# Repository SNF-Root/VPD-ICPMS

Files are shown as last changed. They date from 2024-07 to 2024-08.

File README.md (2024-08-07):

# Low-Cost, DIY Vapor Phase Decomposition (VPD) Scanner for Trace Metal Detection on Surface of Wafers

*Insert GIF of the scanner operating*

## Introduction
Vapor phase decomposition (VPD) is a process used in the semiconductor industry to quantify trace metal contaminants on the surface of wafers. This GitHub repo provides the first open-source instructions to manufacture, program, and install a VPD capable of XXX atoms/CM^2 measurements for academic cleanrooms. 

This project was created by Alex Denton, Trevor, and Thomas Rimer at the [Stanford Nanofabrication Facility](https://snf.stanford.edu/). All ICP-MS analysis was performed by Karrie Weaver and Kathleen Akbar at the [SIGMA lab](https://sigmalab.stanford.edu/).

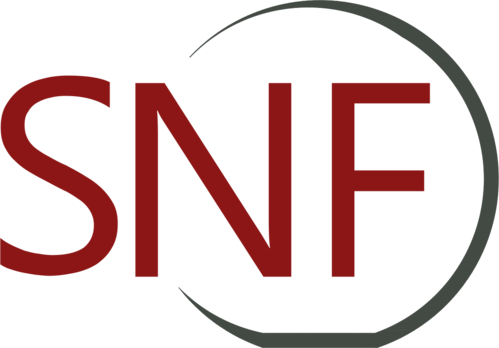
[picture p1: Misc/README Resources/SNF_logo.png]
SNF Logo
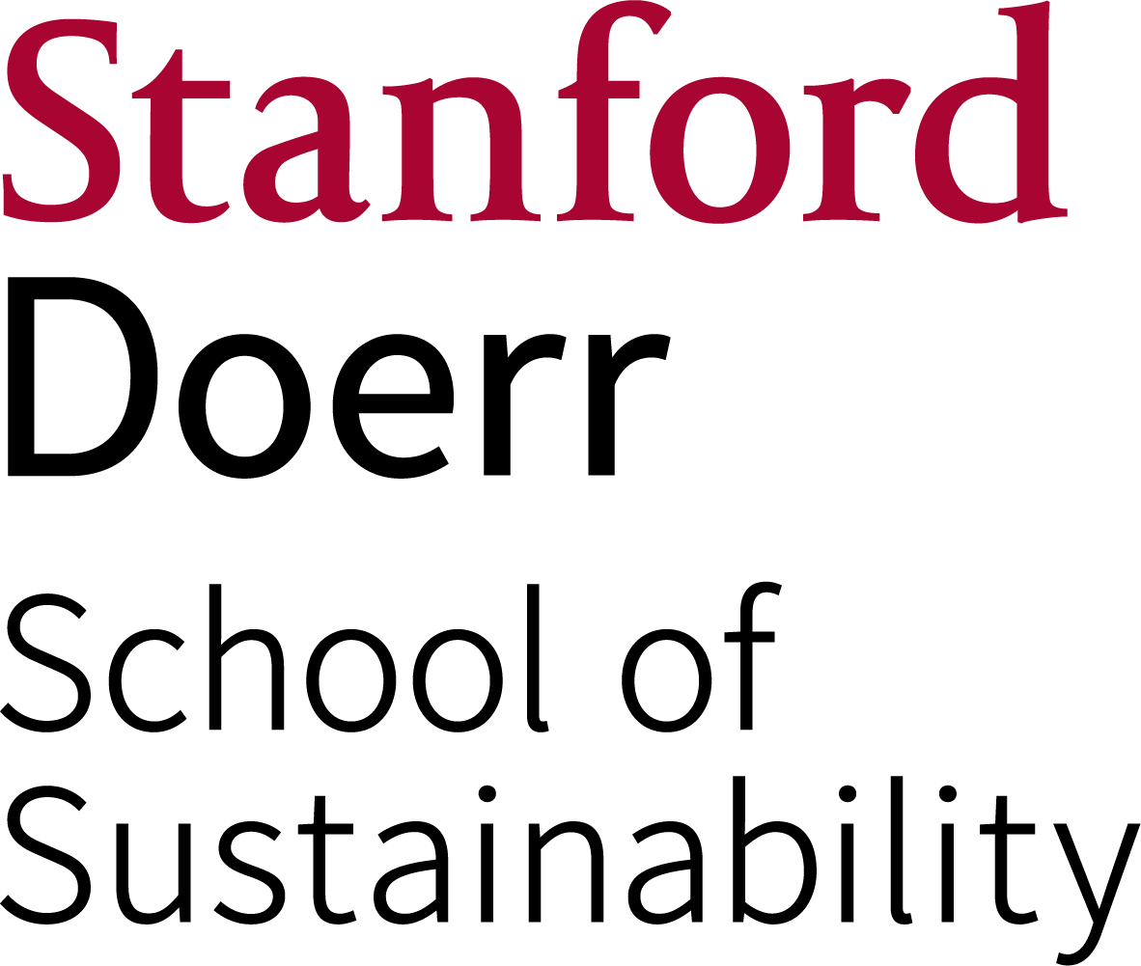
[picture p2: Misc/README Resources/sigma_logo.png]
SIGMA Logo
 

## Overview

*Insert image of the scanner sitting inside its box in a fume hood*

VPD (vapor phase decomposition) is a technique to collect metal and chemical contamininats on the surface of a wafer into a liquid droplet. The details of this collection process are explained in the "Operating Principles Section" right below. Crucially, VPD *does not* involve the measurement or quantification of chemicals; it's simply a technique (among many) to collect them. That's where ICP-MS comes in...

ICP-MS stands for "Inductively Coupled Plasma Mass Spectroscopy." It's one of the most sensitive techniques for measuring the concentration of metals and other chemicals in liquid solutions. Check out [this video](https://www.youtube.com/watch?v=tP5ZKUTWiuQ) from Agilent (an ICP-MS tool manufacturer) to learn about the basic operating principles of an ICP-MS. Briefly, the liquid sample is aerosolized before getting ionized by a plasma. Metals in the solution are then sorted and counted based on their charge/mass ratio. 

When VPD and ICP-MS are combined, it's called VPD-ICP-MS. Note that VPD doesn't necessarily need to use ICP-MS for analysis; alternatives like Atomic Absorption Spectroscopy (AAS) are also common. Similarly, VPD is not the only way to collect samples for ICP-MS; anything from blood to seawater to colloidal space dust can be measured in an ICP-MS.

Using the provided instructions outlined below, the entire VPD scanner and its enclosure can be built in <XXX hours for $X,XXX. Detailed information on the VPDs performance is availible in the [Performance](#performance) section.

## Operating Principles

The VPD scanner is based on a modified 3D printer; instead of a hot-end to extrude plastic, it has a motor-controlled syringe. To scan a wafer, the syringe first aspirates ~200 uL of an HF/H2O2/Water solution. Then it lowers to the surface of the wafer and dispenses the solution, forming a droplet on the surface of the wafer. Crucially, the droplet remains connected to the tip of the syringe. Over the course of 5-15 minutes (depending on wafer size), the scanner slowly moves the syringe head in a series of expanding concentric rings, dragging the droplet across the entire surface of the wafer. The HF in the scan solution attacks the ~2nm native oxide on the wafer's surface, dissolving any contaminants on the surface (and first few layers of SiO2). Finally, the scanner sucks up the droplet from the surface and dispenses it in a collection cuvette, for later analysis by an ICP-MS.

This droplet-dragging technique is similar to what's found in commercial VPD machines. However, there are a few differences worth noting:

**Vapor Etching:** As the name "Vapor Phase Decomposition" might suggest, commerical VPDs use an HF vapor to etch the entire surface of the wafer at once, before the droplet scan commences. This VPD scanner relies on aqueous HF within the scan solution to etch and collect the contaminants at the same time, avoiding the vapor etching step.

**Full Automation:** A human user is needed for setup and sample transfer for this DIY VPD. Most commercial VPDs have fully automated setups which allow for seamless integration into production lines.

**Speed:** While our machine takes ~20+ minutes to process a wafer, a commercial machine can often complete a scan in <60 seconds.

## Imporant Notes

**Analysis**: As hinted at above, this project assumes you have access to an ICP-MS or similarly sensitive tool to analyze the samples. The VPD scanner itself has no capacity to analyze the droplets it collects. More information about the ICP-MS analysis—along with alternatives—are detailed in the XXX section below. 

**Safety**: This project relies on hydrofluoric acid (HF) for the collection solution. HF is an extremely toxic chemical; if you need to google why, this project is *not* for you.

**Setup**: This machine produces HF vapor and should therefore be operated inside a fume hood. The minimum fume hood space required is 20" wide, 25" deep, and 42" tall. Note that the enclosure built for the scanner (detailed below) is NOT a fume hood; it is a positvely pressurized chamber to keep the VPD free of contaminats. If the enclosure is placed outside of a fume hood it will pump HF fumes at the operator and surrounding environment!

## DIY VPD Instructions

The rest of this document is dedicated to the detailed instructions for fabricating, testing, and using your own DIY VPD. 

0. [Fabrication Overview](#step-0-fabrication-overview)
1. [Procurement](#procurement)
2. [Manufacturing and Assembly](#manufacturing-and-assembly)
3. [Scripting](#scripting)
4. [Characterization](#characterization)
5. [Standard Operation](#tunning-your-first-test)
6. [Misc](#mis)

## Step 0: Fabrication Overview

The fabrication, setup, and programming of the machine are as follows:
1) First, all supplies need to be purchased. This is thoroughly explained in [Procurement](#procurement)
2) Next, both parts of the VPD need to be built: the scanner (which scans the droplet) and the enclosure (which forms a clean environment around the scanner). Instructions are layed out in [Manufacturing and Assembly](#manufacturing-and-assembly)
3) After building the VPD, it needs to be programmed. [Scripting](#scripting) explains the tradeoffs between pre-generated scripts and writing custom programs.
4) With the VPD fully operational, it needs to be characterized. This involves "recovery tests" which directly measure how precise the VPD is and help diagnose hidden performance issues like contamination. The steps are outlined in [Characterization](#characterization).
5) After characterization, the VPD is ready for users! [Standard Operation](#tunning-your-first-test) offers advice on installement, intermittent calibration, and other practical guidelines for transporting samples to the ICP-MS for analysis. 
6) [Misc](#misc) contains credit and license information.

All aspects of the manufacturing process are designed to be as accessible as possible. However, it's assumed that some basic tools are availible for fabrication. Below is a list of the required materials:

- 3D printer (minimum bed size: 8" x 8" x 3")
- Laser cutter (minimum bed size: 24" x 20")
- Phillips screwdriver
- Metric allen keys
- Soldering iron
- Scissors
- Tape

### Contact Us

If you've read this far, you're probably pretty interested in VPD. Please reach out if you're thinking about building a scanner, have questions about the build process, or have issues with your own DIY-VPD! We're excited to get these into as many labs as possible! We ask you use the "Issues" tab on GitHub to ask questions (even if it's not strictly an "issue"). This will allow other people thinking of building a VPD to see who else is interested, what they're thinking, and problems they're encountering.

## Step 1: Procurement

*Every good project starts with a McMasterr Carr order; the VPD scanner is no different.*

Below are three tables, each with a set of components. The "Scanner Components" are used to build the scanner itself. The "Enclosure Components" are used to build the enclosure around the scanner. The "Experimentation Supplies" are the consumables needed to actually run experiments. All prices are approximate, as of July 2024.

All components in the first two tables can be purchased from  McMaster Carr or Amazon. However, the strict purity requirements for the sample collection means many of the experimentation supplies must be ordered directly from suppliers.

Note that each section has dropdowns that go into further detail on different items, including alternative recommendations.

### Scanner Components
| Item | Price per Unit | Units | Subcost | Link | Use
|----------|----------|----------|----------|----------|----------|
| Ender 3 3D Printer    | $249     | 1     | $168 | [Amazon](https://www.amazon.com/Comgrow-Creality-Ender-Aluminum-220x220x250mm/dp/B07BR3F9N6/) | Sacrifical 3D printer converted into the scanner
| Filament    | $25     | 1     | $25 | [Amazon](https://www.amazon.com/HATCHBOX-Printer-Filament-Dimensional-Accuracy/dp/B09G85F1CC/?th=1) | Material used to print the necessary Ender modifications

Scanner Components Subtotal: **~$200**

<details>
  <summary> Click here for details about Scanner Components, alternatives to certain items, and other comments</summary>
   
  ### Ender 3 S1 3D Printer
  The Ender 3 is a super popular, low cost, easily modifiable 3D printer chosen for its large support community and easily accessible components.

  **Ordering notes**: Feel free to purchase the Ender 3 from any website. Note that there are different versions of the Ender 3 (Ender 3s, Ender 3 pro, etc...) Make sure you purchase the Ender 3 to ensure the syringe head 3D prints fit the gantry. If you do order from a different supplier, make sure it comes with a MicroSD card. If not,  order a micro SD card seperately.
  
  **Alternatives**: Using any other 3D printer will almost certainly mean a complete redesign of all mechanical components, including the clean enclosure (unless the alternative printer is smaller than the Ender 3). Additionally, the scan programs would no longer work, meaning you'd need to generate your own using the custom routine builder included in this repo. If there were one component in this build we'd suggest not replacing, it's the Ender 3 printer. 

  ### Filament
  **Ordering notes**: Any brand of 3D printer filament will work just fine. Because the 3D prints should never come in contact with the scan solution, it does not matter what plastic you use. We recommend PLA for its ease of printing. However, PolyMax filament from PolyMaker has repeatedly proven itself as the most durable filament based on our testing, so we think it's worth purchasing. 
  
  **Alternatives**: If you're feeling ambitious, some/all 3D printed components can be machined out of teflon. This will provide excellent chemical resistance and durability. Stanford actually has a version of the scanner with custom machined teflon components. Finding a teflon machine shop, creating engineering drawings, and managing the manufacturing process is not discussed in this guide.
</details>

### Enclosure Components
| Item | Price per Unit | Units | Subcost | Link | Use
|----------|----------|----------|----------|----------|----------|
| Acrylic Plastic Sheet    | $57     | 7     | $400 | [McMaster](https://www.mcmaster.com/8560K357/) | Clear panels cut to form enclosure walls. 24"x24", 1/4" thick
| Blower fan    | $92     | 1     | $92 | [McMaster](https://www.mcmaster.com/2059K36/) | Forces air through the filter, positively pressurizing the enclosure
| ULPA Filter    | $285     | 1     | $285 | [McMaster](https://www.mcmaster.com/5543N11/) | Removes 99.999% of particulate <0.3um in the air entering the box
| Teflon Film    | $21     | 3ft     | $63 | [McMaster](https://www.mcmaster.com/8569K63/) | Protects enclosure against HF splashes
| Slow Cure Epoxy    | $14     | 1     | $14 | [Amazon](https://www.amazon.com/Bob-Smith-Industries-BSI-205-Slow-Cure/dp/B0166FFFS4/) | Joins the acrylic side panels together
| Magnets    | $0.90     | 16     | $14 | [McMaster](https://www.mcmaster.com/5862K103/) | Magnetically joins the front panels to the enclosure box
| Fast Cure Epoxy Resin    | $5     | 1     | $5 | [Amazon](https://www.amazon.com/Gorilla-Epoxy-Minute-ounce-Syringe/dp/B001Z3C3AG/?th=1) | Bonds 3D prints to the acrylic enclosure sidewalls
| Silicone Caulk    | $7     | 1     | $7 | [Amazon](https://www.amazon.com/GE-Advanced-Silicone-Kitchen-Bathroom/dp/B0C9VYYCPB/?th=1) | Non-permanent bond for filter components
| 12v Power Supply    | $26     | 1     | $26 | [Amazon](https://www.amazon.com/LRS-200-12-Switching-Supply-Single-Output/dp/B0131UU9E2/?th=1) | Powers the blower fan and LED strips
| LED Light Strip    | $21     | 1     | $21 | [Amazon](https://www.amazon.com/TOPAI-Waterproof-Brightness-2400LEDs-Cuttable/dp/B0BVR996T2/) | Illuminates inside of the box
| Power Switch    | $8     | 1     | $8 | [Amazon](https://www.amazon.com/mxuteuk-Illuminated-Household-Appliances-MXU3-101NR/dp/B07QQ21CZD/) | Toggles power to enclosure and scanner
| Power Cable    | $6     | 1     | $6 | [Amazon](https://www.amazon.com/Amazon-Basics-Computer-Monitor-Replacement/dp/B072BYGKZZ/?th=1) | Cannabilized into master power cable for scanner and enclsoure

Enclosure Components Subtotal: **~$950**

<details>
  <summary> Click here for details about Scanner Components, alternatives to certain items, and other comments</summary>
   
  ### Acrylic Plastic Sheets

  **Ordering notes**: Minimum sheet size is 23.5" x 19.5." We recommend NOT purchasing the plastic through McMaster. Instead, find a local plastic shop or hardware store that sells acrylic sheets. We purchased all our acrylic from TAP plastics; if you're in the San Francisco Bay Area, this is by far the best place to pick up material. Local shops will also cut stocks down to a size convenient for you; for example, we had TAP cut all our acrylic down to 32"x20" sheets to fit our laser cutter. 
  
  **Alternatives**: As the most expensive building material, it's tempting to find alternatives. Theoretically, any plastic enclosure that can fit the 3D printer inside and can have holes cut in it for ventilation would work. However, the clear material makes viewing the operation of the machine much easier. 

  ### Blower Fan

  **Alternatives**: If you plan on using a different blower fan, know that there are a few important considerations. First, make sure it runs on the same voltage as the power supply (and thus by extension LED lights) to avoid needing a second PSU. Second, a multi-speed blower fan is ideal to allow standby and operating blowing speeds. Lastly, a different blower fan will need a redesigned fan shroud to couple the fan output to the ULPA filter.

  ### ULPA Filter
  
  A ULPA filter was selected over a HEPA filter for its increased filtering power. We recommend using ULPA filters to lower the chance of airborne contaimination. 

  The ULPA filter linked in the table is very large and should last for years. Base your spare ordering on that working time. For what it's worth, Stanford did not purchase any spare filters.

  **Alternatives**: If you have spare, clean ULPA filters availible from another source, feel free to use them. Just note that you will need to change both the hole size in the top of the container and fan shround to couple the blower air into the filter. Also make sure the filter is not too restrictive to air flow, else you'll need to replace the blower fan.

  ### Teflon Film

  Teflon is one of a few materials resistant to HF, so this thin sheet will sit on the bottom of the acrylic enclosure to protect it from minor HF splashes.

  **Ordering Notes**: The protective sheet used on the bottom must be made from teflon. However, any brand or supplier will work fine. 

  ### Slow Cure Epoxy

  This slow cure epoxy has a long working time allowing you to fully assemble the enclosure with epoxy in the joints before it cures.

  **Alternatives**: Any long-cure (>30 min working time) will work. For aesthetic reasons we recommend a clear-drying epoxy. When building enclosures with acrylic, it's also common to see acrylic cement used; we attempted this with our enclosure and decided not to use it due to the strict edge flatness requirements. We would discourage working with acrylic cement unless you are already familiar with it. Do NOT try and use quick curing epoxy to build the enclosure, it will set before you finish assembling the enclosure.

  ### Magnets

  **Ordering notes**: The magnets are so inexpensive we recommend ordering and using the suggested ones.

  ### Fast Curing Epoxy Resin

  Rather than the slow curing epoxy, this resin is used for joining the plastic 

  **Ordering Notes**: Brand or size of epoxy resin does not matter; it will work so long as it's a general purpose epoxy designed to bond metal and plastic.

  **Alternatives**: Feel free to not order any fast curing epoxy and instead use the slow curing epoxy. Just know you'll need to wait longer for plastic parts to adhere to the acrylic, which means you'll probably need to tape them on (rather than being able to hold them against the the walls).

  ### Silicone Caulk

  **Ordering Notes**: Brand or size of the silicone caulk does not matter; feel free to purchase from a local hardware store or use a tube laying around the lab (as long as it hasn't gone bad).

  ### Power Supply

  **Ordering Notes**: Any 12v power supply will do as long as its current rating matches or exceeds the sum of the blower fan and LED light requirements.

  **Alternatives**: If you use a different LED light strip or blower fan that does not use 12v, you will need to find a new power supply accordingly. The common, rectangular, thin power supply housing type (same as the PSU linked in the table) is preferred due to its ease of mounting on the back of the ULPA filter later on.

  ### LED Lights

  While the LED lights are not necessary, they improve visibility of the VPD scanner and make it cooler.

  **Ordering Notes**: Any LED light strip with the same voltage as the power supply will work fine.

  **Alternatives**: Any lighting (bulb, lamp, etc...) that operates on either 120v or the power supply voltage will work.

</details>

### Experimentation Supplies
| Item | Price per Unit | Units | Subcost | Link | Use
|----------|----------|----------|----------|----------|----------|
| 1mL Syringes    | $29     | 1     | $29 | [Amazon](https://www.amazon.com/Syringe-Luer-Slip-Plastic-PK100/dp/B0763KTQV5/) | Pack of 100 polyethlyne syringes. Mounts inside the scanner to aspirate, move, and dispense droplet.
| Teflon Cuvette    | $--     | -     | $-- | [Amazon]() | Sterile container for both the scan soltion and scanned droplets
| Teflon Jar    | $--     | -     | $-- | [Amazon]() | Sterile container to prepare HF and H2O2 scan solution 
| Ultrapure HF    | $---     | -     | $--- | [Amazon]() | Ultrapure 2% HF to prepare scan solution
| Ultrapure H2O2    | $---     | -     | $--- | [Amazon]() | Ultrapure H2O2 to prepare scan solution
| MS Standard Solution    | $---     | -     | $-- | [Amazon]() | Pre-made solution containing ~24 heavy metals for characterizing VPD

Experimentation Supplies Subtotal: **~$1,500**

<details>
  <summary> Click here for details about Experimentation Supplies, alternatives to certain items, and other comments</summary>
   
  TODO: Complete ordering details once testing is finished and part suppliers are finalized.

</details>

## Step 2: Manufacturing and Assembly

*Insert labeled rendering of the final assembly*

The VPD scanner has two sub assmblies; the scanner and the enclosure. Each can be built independently of the other, making it convienent to split up amongst multiple people.

There are XX 3D prints requried for this project. To minimize the amount of time spent waiting for 3D prints to finish, we recommend printing all the parts before beginning any other manufacturing and assembly. 

Tehcnically, you can 3D print all components on the Ender 3 printer purchased for the scanner. This is recommended only if you have limited access to other printers. If you decide to 3D print the components on the Ender 3, you should first fully assemble the 3D printer following the video in [Step 2.1](#step-2-1) (not skipping any steps). Then, print all components (as outlined below) before continuing on the project. Know that once you've modified the printer into the scanner, it will take around an hour to uninstall the VPD parts and restore the Ender to a print-worthy state. 

<details>
  <summary> Click here for a complete list of required 3D printed parts, their associated quantities, and recommended print settings/orientations</summary>
   
  TODO: Add the complete list of STL files and how many need to be made.

</details>

### 2.1 Scanner Manufacturing

*Insert photograph of finished scanner*

#### Step 2.1.1: Assembling the Ender 3s

The Ender 3s comes partially assembled from the factory. There are several high-quality YouTube tutorials already made outlining exactly how to assemble an Ender 3. Here's a well-made one from [3D Printing Canada](https://www.youtube.com/watch?v=dQ0q9zLygTY) (https://www.youtube.com/watch?v=dQ0q9zLygTY).

While most of the build proceeds as normal, there are a few steps you should <ins>not</ins> do:

- Do not install the spool holder.
- Do not mount the extruder stepper motor on the bracket designed for it. However, you should still wire the stepper to the controller board. The extruder stepper motor will be used later on to control the syringe.
- Similarly, do not install the spring-loaded extruder gear assembly. This is not needed for the VPD.
- Do not mount or screw in the bed leveling adjustment dials. These will be installed later.
- Do not binder-clip the Ender-branded build surface onto the print bed. Parts will mount directly onto the print bed later, so this build surface is not needed.

Save all components (and spare parts) that you do not install. You will need some of these materials later.

#### Step 2.1.2: Print and Install Parts For Wafer Holder

There are three necessary 3D printed components for the wafer holder, and an additional five optional 3D printed components:

Required
- 001_Wafer_Holder_Base.stl
- 002_Wafer_Vial_Holder_Left.stl
- 003_Wafer_Vial_Holder_Right.stl

Optional
- 004_Wafer_Holder_2_inch_Chuck.stl
- 005_Wafer_Holder_3_inch_Chuck.stl
- 006_Wafer_Holder_4_inch_Chuck.stl
- 007_Wafer_Holder_5_inch_Chuck.stl
- 008_Wafer_Holder_6_inch_Chuck.stl

<details>
  <summary> Click here for a details about 3D printing orientation and settings
  <br></br>
  </summary>
   
  TODO: Include pictures of recommended print orientation and print settings for the  components. This should be a copy from the complete 3D print list above.

</details>

At least one optional component must be printed to use the wafer holder. 

Place 001_Wafer_Holder_Base on the print bed, alligning the the holes in each corner with the screws holes in the aluminum bed. The two cylindrical cavities should face the front of the printer. The two lock diagrams should be in the back of the printer. Slide the included bed-leveling screws through the four screw holes in each corner of the Wafer Holder Body, making sure it also goes through the metal print bed. Underneath each corner, slide a bed leveling spring onto the screw stick out. Then twist on a large bed leveling dial (included with the Ender) onto each corner. Tighten until there are a few phillips threads visible sticking out past the dial. Precise adjustmenet of the bed leveling dial will occur later.

*Include image of the 3D printed base on the print bed with screws through them. Include side image of the dial on the phillips screw with spring in proper compression*

All 5 of the optional wafer chucks are adapters designed to hold specific diameters of wafer. Print whichever sizes you anticipate needing to scan (Stanford printed all 5 of them just in case).

*Include image of installed 6" chuck*

The wafer chuck twists into place on the base. To install a chuck, place it on the base 45° off from the base such that the small bump in the middle of the base intefaces with the divot on the underside of the chuck. Rotate the chuck counter clockwise, causing the dovetails on each arm of the base to interface with the slots on the chuck. Continue twisting until the chuck flushly sits atop the base.

To uninstall a chuck, simply press the chuck in the clockwise direction. It should pop out easily. Sometimes, it can help to press on two arms at once.

#### Step Step 2.1.3: Print and Install Parts For Syringe Head

There are three 3D printed components required for the syringe head:

- 0XX_Syringe_Holder_Body.stl
- 0XX_Syringe_Holder_Rack.stl
- 0XX_Syringe_Holder_Pinion.stl

<details>
  <summary> Click here for a details about 3D printing orientation and settings
  <br></br>
  </summary>
   
  TODO: Include pictures of recommended print orientation and print settings for the  components. This should be a copy from the complete 3D print list above.

</details>

First, use three XX mm long MX screws included with the hot end to mount the Syringe Holder Body onto the gantry, as pictured below.

*Include image of the syringe holder body mounted on the gantry*

Next, use XXX M3 screws included with the extruder stepper motor to mount the extruder stepper motor onto the backside of the syringe holder body, as pictured below. Make sure the stepper motor cable points in the direction away from the LCD panel. 

*Include image of the syringe holder body and stepper motor*

Press fit the 3D printed pinion on to the stepper motor shaft. It should fit snuggly. If the pinion is too loose, wrap a layer of tape evenly around the shaft and try press fitting again. If the pinion does not fit on the shaft (hole is too small), file/sand down the hole until it fits.

*Show image of the pinion press fit onto the stepper shaft*

Lastly, slide the rack into the syringe holder body. Insert the two dovetails on the back of the Syringe Holder Rack into the dovetail slots on the top of the Syringe Holder Body. Press the rack down until its teeth make contact with the pinion. Continue pushing the rack down, causing the pinion to interface with the rack and begin spinning. Push the rack all the way down until the small arm collides with the Sryinge Holder Body's ledge and prevents it from going further. There should be some friction/resistance to pressing the dovetails together, especially the first time they're connected. 

*Show two images of the rack, one of it getting inserted into the top, and the other of it bottomed out.

#### Step Step 2.1.3: Print and Install Fan Ducting

There are two 3D printed ducts required for the printer:

- 0XX_Controller_Duct.stl
- 0XX_Power_Supply_Duct.stl

<details>
  <summary> Click here for a details about 3D printing orientation and settings
  <br></br>
  </summary>
   
  TODO: Include pictures of recommended print orientation and print settings for the  components. This should be a copy from the complete 3D print list above.

</details>

These ducts prevent dust raised from the 3D printer's cooling fans from contaminating the interior of the clean enclsoure. 

To mount the controller duct, apply silicone to the hatched, flat face on the controller duct 3D print. Press the duct on to the controller housing such that to encapsulates the fan exhaust port, and the other end of the duct points to the left side of the machine. Tape the duct in place while the silicone cures to prevent the duct from falling over. 

*Include an image of the installed controller duct*

To mount the power supply duct, apply silicone to the hatched, flat face on the power supply duct 3D print. Press the duct onto the silver power supply such that the duct runs down the power supply and exhausts next to the base of the printer. Tape the duct in place while the silicone cures to prevent the duct from sliding down the power supply.

*Include an image of the installed power supply duct*

### 2.2 Enclosure Manufacturing

*Insert CAD rendering of finished enclosure*

The enclosure is built from laser-cut acrylic panels. A fan mounted on top of a ULPA filter blows clean air into the top of the enclosure. Slots cut into the bottom of the enclosure allow the clean air to escape out the bottom, ensuring laminar, downward flow throughout the entire box. A power supply mounted on the back of the ULPA filter powers the fan and LED lights. The box and scanner is enabled/disabled by a single power switch mounted on the side. The front panel is split in three parts, all mounted on the front of the box by magnets. This allows easy access during routine operation, and the ability to completely remove the scanner during installation and cleaning. The bottom of the enclosure has a teflon film to protect the acrylic from HF splashes.

The complete CAD assembly is availible in the CAD/enclsoure folder. All individual parts are also availible as STEPS files, STLs, OBJs, and F3Ds.

**Step 2.2.1: Cutting Acrylic Panels**

There are 8 acrylic side panels that must be cut from the acrylic sheets:
- Left panel
- Right panel
- Back panel
- Bottom panel
- Top panel
- Front top panel
- Front middle panel
- Front bottom panel

All patterns for the panels are in the [XXX/XXX folder](). Each panel is provided in both DXF and SVG format.

We  strongly suggest using a laser cutter to cut the acrylic side panels. Stanford used a 120 watt Trotec SP500 Laser Cutter to make all the panels, which took about 3 hours. Nearly every university has a maker space with a free-to-use laser cutter. 

The layout of the panels on the acrylic sheets depends on the size of the acrylic sheets (which in turn cannot be any larger than the bed of the laser cutter). The acrylic sheets Stanford purchased were 32"x20". Thus, the following layout was used.

*Insert screenshot of the lasercutting layout*

As mentioned in the drop down section under Enclosure Components, the largest panels for the enclosure are 23.5" x 19.5". Make sure your laser cutter bed is large enough to accomodate those panels, and the acrylic sheets you purchase are also larger.

When cutting the panels with the laser cutter, do your best not to position the cuts right along the edge of the acrylic side panel. The laser used to cut the plastic has a certain cutting width which affects the final dimensions of the part by a few tenths of a mm. The enclsoure was designed to cancel out these errors, so long as all edges are affected the same amount. If some of the panel edges are laser cut and others are saw cut (from the factory/store), you may end up with gaps that make assembly harder.

*Include image showing proper and improper arrangement of panels relative to plastic sheet*

If desired, a custom logo can be engraved in any of the side panels for decoration. Stanford etched the "SNF" logo onto the left panel. This is totally optional but can make the enclsoure look even better.

**Step 2.2.2: Acrylic Enclosure Bonding**

To bond the enclosure together, we recommend first doing a practice run with just tape. It's best to addemble the enclosure with two people (so someone can hold a side panel while the other person tapes it). Below are instructions paired with CAD renderings of the enclosure bonding process. Note that colors are for illistrative purposes.

Begin by placing the base panel on a large, flat table. 

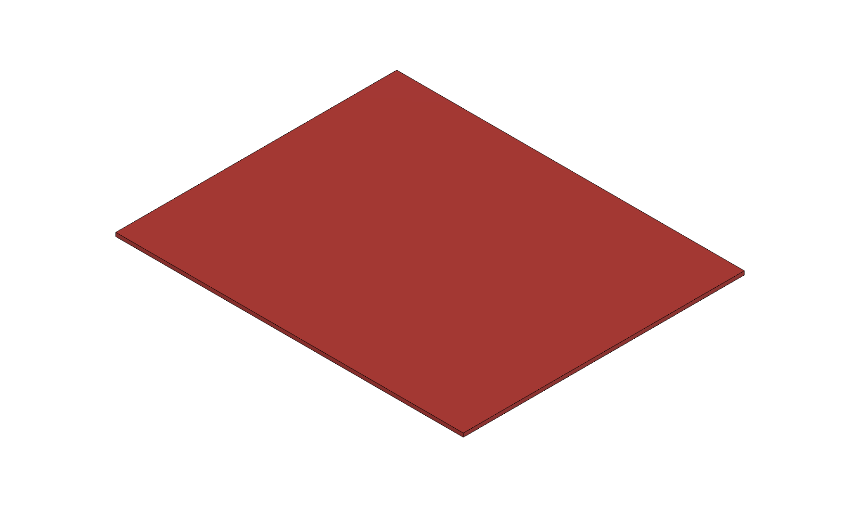
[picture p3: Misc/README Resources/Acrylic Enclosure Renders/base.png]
Base


Next, stand up the right panel on a long side of the base. The vents should be close to the base. The right panel should be flush with the side of the base, and each end of the right panel should line up with the front and back of the base. The rounded rectangular hole denotes the back of the enclosure. 

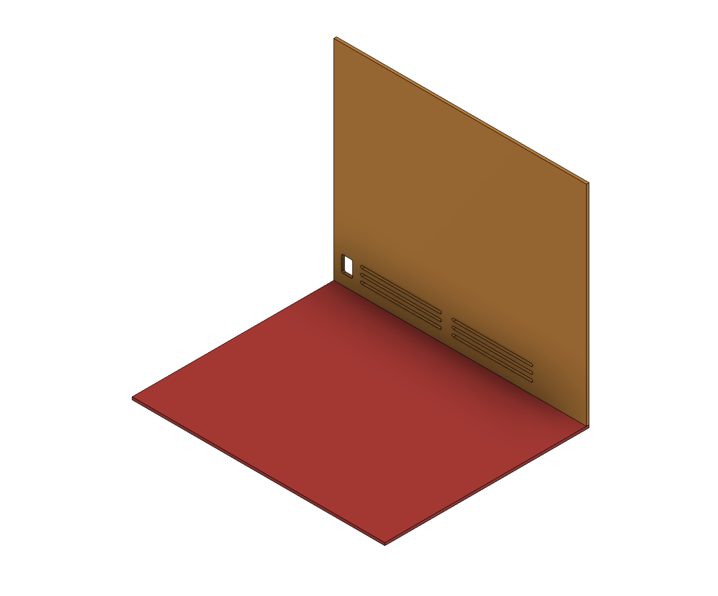
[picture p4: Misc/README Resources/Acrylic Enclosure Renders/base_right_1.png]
Base and Right Panel 1
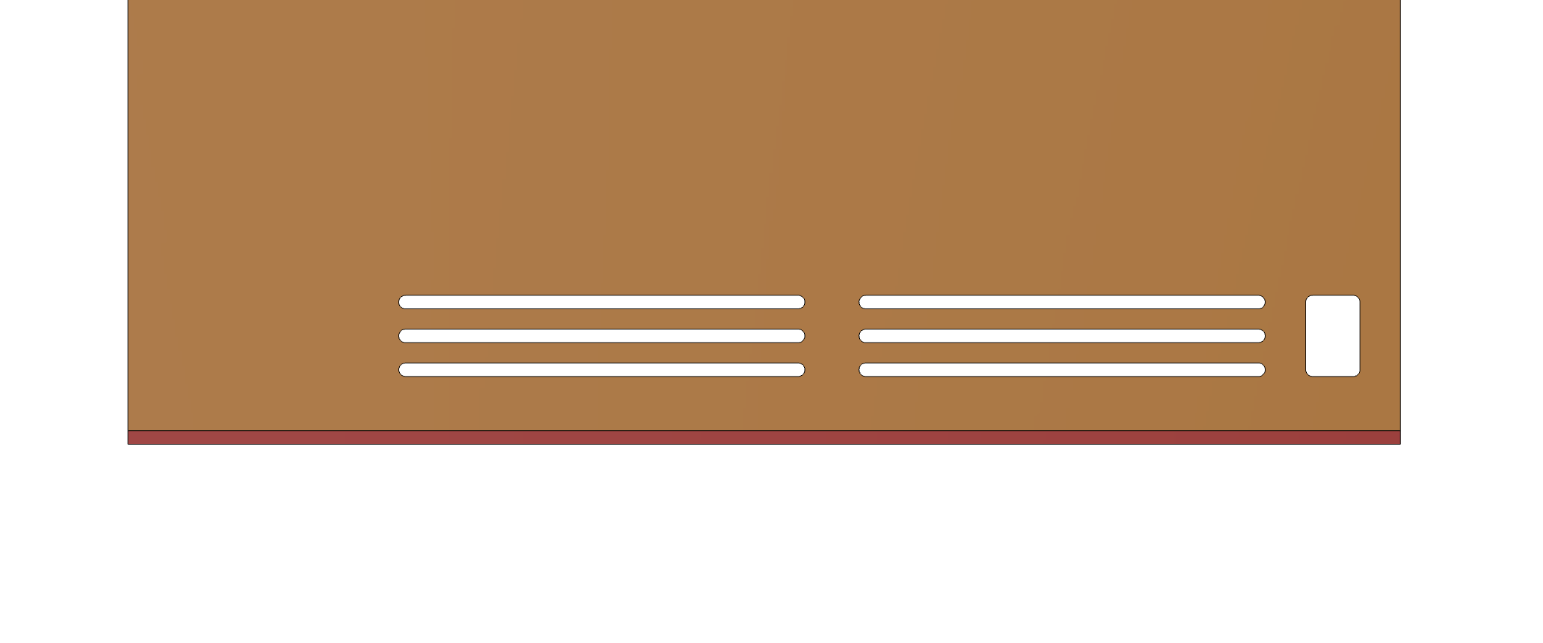
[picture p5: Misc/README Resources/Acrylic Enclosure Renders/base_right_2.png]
Base and Right Panel 2
 

Next, stand up the back panel along the back side. The back panel should be flush with the back edge of the base, and the right end of the back panel should be flush against the inside of the right panel. The vents should be at the bottom. The left end of the back panel should not be flush against the left edge of the base (there is a 1/4" gap for the left panel to mount). Use small pieces of masking tape on the outside of the enclsoure to secure the right and back panels to the base, as well as to one another. After taping, the enclsoure should be able to stand on its own. 

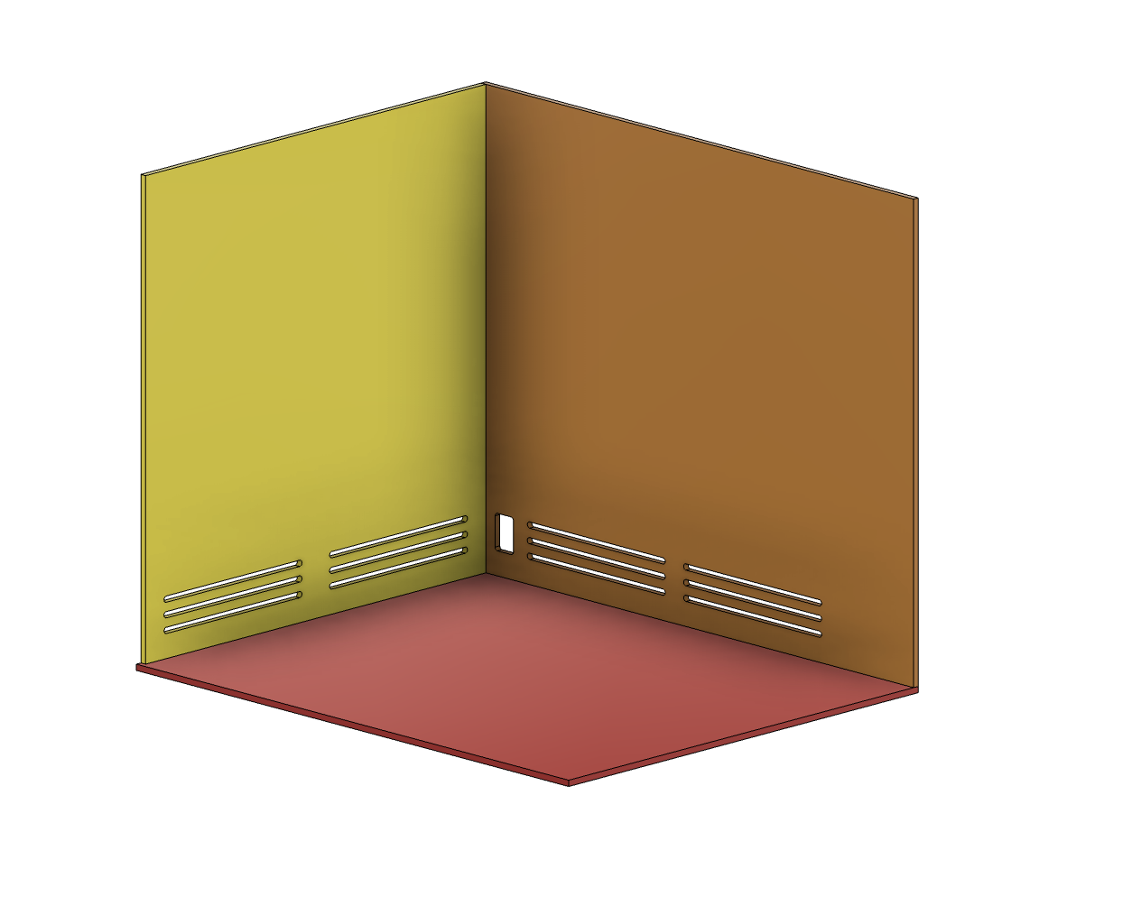
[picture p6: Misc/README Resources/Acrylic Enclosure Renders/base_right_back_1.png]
Base, Right, and Back Panel 1
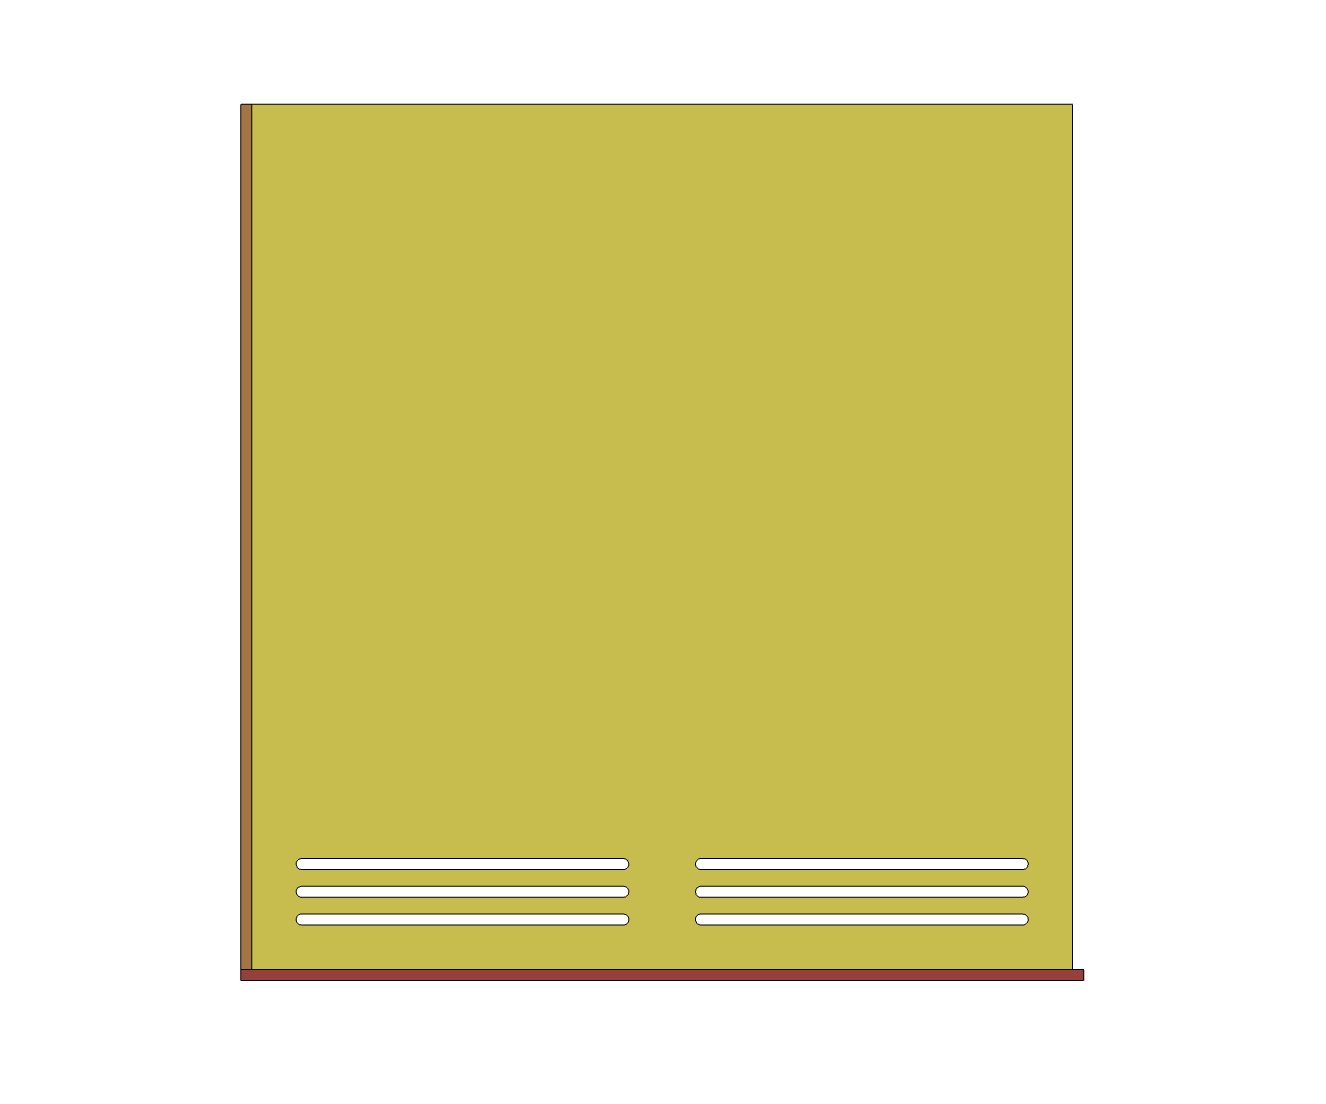
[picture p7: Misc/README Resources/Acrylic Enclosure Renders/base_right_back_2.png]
Base, Right, and Back Panel 2
 

Next, stand up the left panel along the remaining long side of the base. It should be in the same orientation as the right side panel, with the vents towards the bottom and the rounded rectangular port in the back. Tape the left side panel to the back and base.

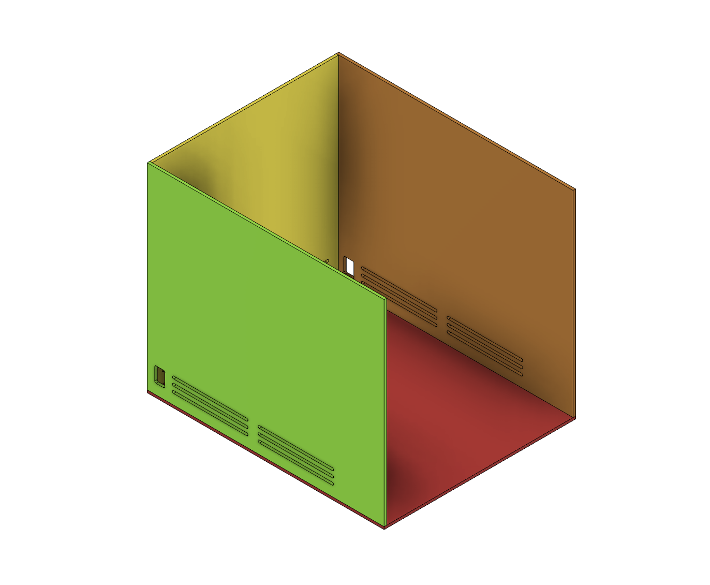
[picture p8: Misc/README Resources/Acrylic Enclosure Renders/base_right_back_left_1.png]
Base, Right, and Back Panel 1
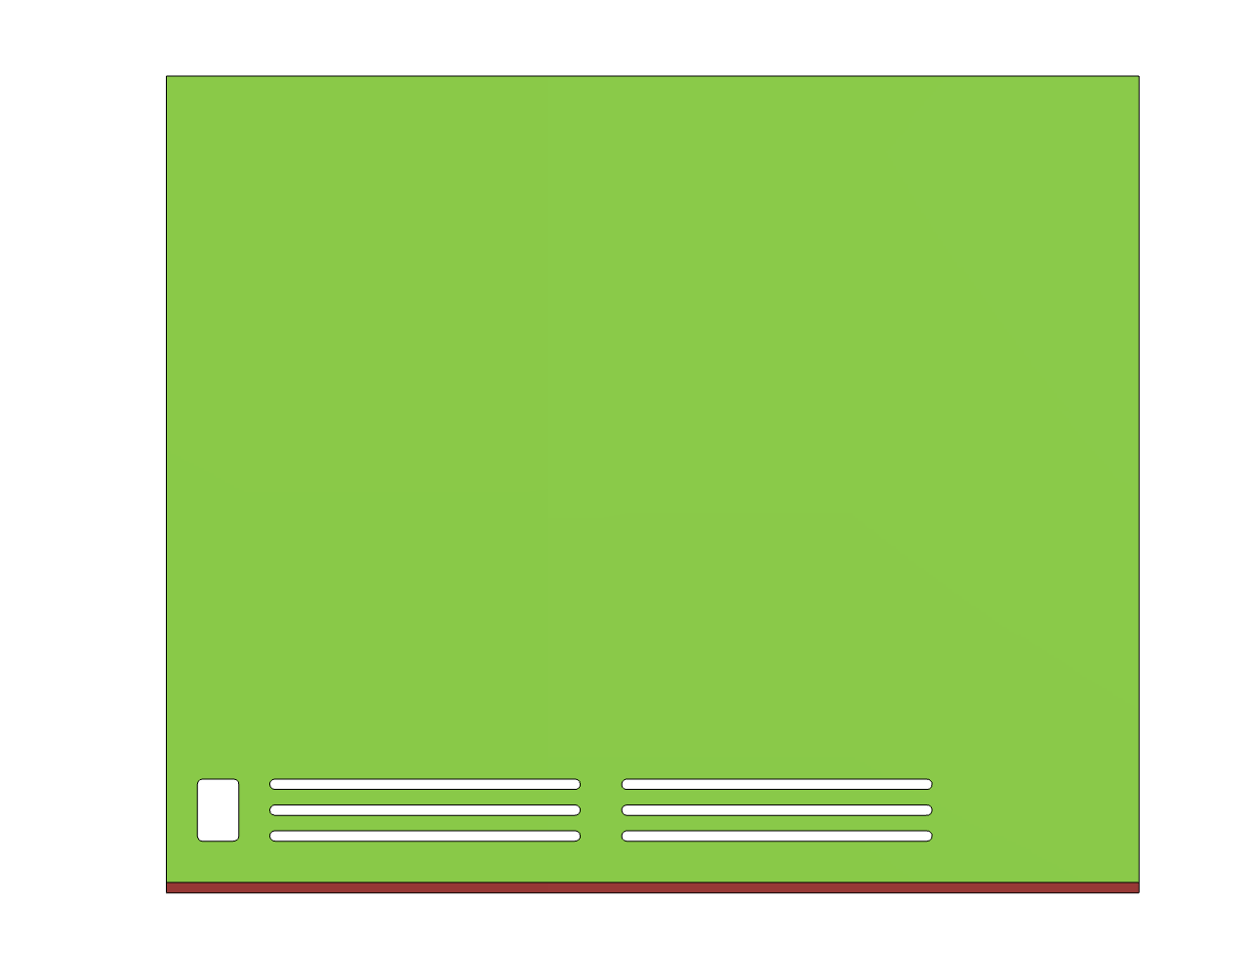
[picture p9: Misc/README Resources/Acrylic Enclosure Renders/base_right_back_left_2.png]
Base, Right, and Back Panel 2
 

Finally, place the top panel on top of the top edges of the left, back, and right panels. If the previous steps were done correctly, all three edges should be level with one another. The small holes in the top panel should be in the back. Tape the top panel on to the left, right, and back panel.

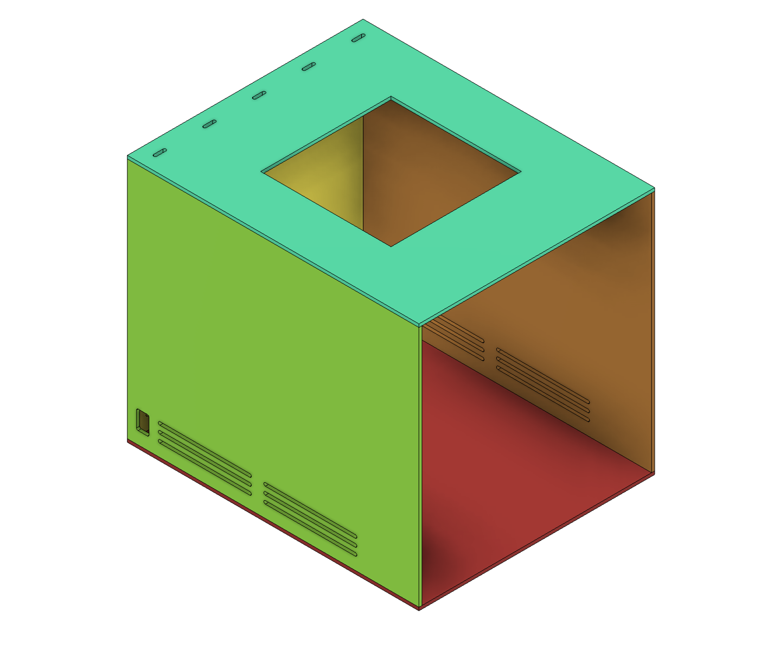
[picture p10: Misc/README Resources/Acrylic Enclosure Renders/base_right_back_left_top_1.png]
Base, Right, and Back Panel 1
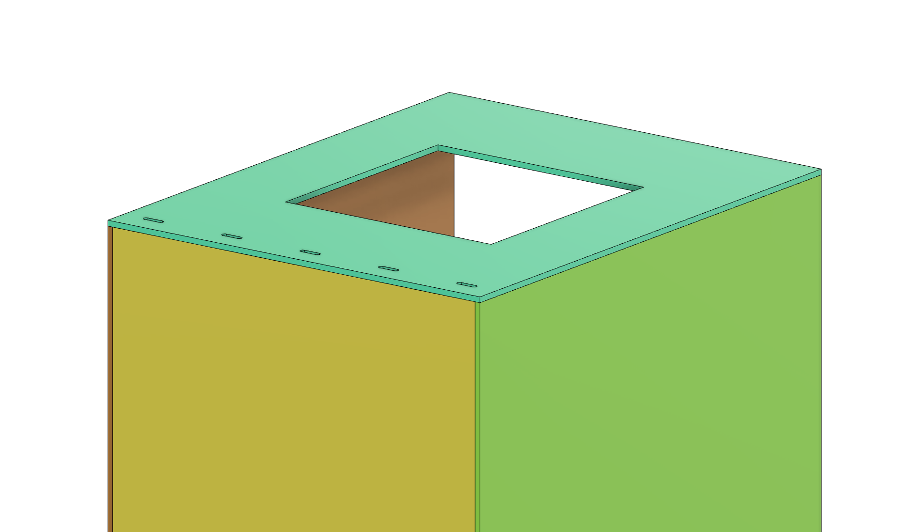
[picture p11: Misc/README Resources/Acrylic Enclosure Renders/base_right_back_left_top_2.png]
Base, Right, and Back Panel 2
 

To permanently bond the pieces, repeat the same taping process, but add epoxy to the edges at each step.

Begin by dissambling the taped structure. When you are ready, mix the long-cure epoxy according to the instructions on its package. You'll have about 15 minutes after mixing to fully assemble the enclosure. Get some friends to help out. Repeat the same taping process described above, but use a popsicle stick or a finger to spread a liberal amount of epoxy along each edge before taping them up. After taping, some epoxy should leach out of the edges. Quickly wipe up the epoxy with a dry paper towel, and follow up with a cold damp paper towel at the end to get any remaining epoxy. 

Leave the box undisturbed in a corner for 24 hours before attempting to remove the tape. It will take a few days before the epoxy has reached its full mechanical strength.

**Step 2.2.3: Mounting Front Panels**

There are eight 3D printed parts required for the front panels:

- 6x 0XX_Magnet_Mount.stl
- 2x 0XX_Handle.stl

<details>
  <summary> Click here for a details about 3D printing orientation and settings
  <br></br>
  </summary>
   
  TODO: Include pictures of recommended print orientation and print settings for the  components. This should be a copy from the complete 3D print list above.

</details>

The front panel is comprised of three smaller sections

- Lower panel (4" tall)
- Middle panel (8" tall)
- Upper panel (8" tall)

Each panel is fixed to the front with a 3D printed magnet mount. This allows for it to be easily removed when accessing or installing the scanner. 

Begin by affixing magnets inside their mounts. Stack all magnets in a stick. This will allign them relative to one another. Mix a small amount of fast cure epoxy and dab it on the bottom of the hole with a toothpick or similar thin object.

**Step 2.2.4: ULPA Filter Installation**

**Step 2.2.5: Blower Fan Installation**

**Step 2.2.6: LED Light Installation**

**Step 2.2.7: Power Switch Installation**

**Step 2.2.8: Power Supply Mounting and Wiring**

**Step 2.2.9: Teflon Base Installation**

### 2.3 Install Scanner Inside Enclsoure

After both the scanner and enclosure have been built, they're ready to be put together!

**Step 2.3.1: Place Enclosure Inside Fume Hood**

The entire clean enclosure must be placed inside a fumehood with proper HF fume extraction to ensure the positively pressurized clean enclosure doesn't poison surrounding users. The minimum required fumehood space is 20" wide by 25" deep by 42" tall.

**Step 2.3.2: Clean the Enclosure**

Use Isopropyl alcohol and a Kimtech (or similar low-lint) wipe to clean all surfaces on the interior of the enclsoure. This prevents dust built up from the fabrication process from dislodging and contaminating the scanner later in its life.

**Step 2.3.3: Clean the Scanner**

For the same reasons as the enclosure, use Kimtech and IPA to wipe down all surfaces on the 3D printer. Particularly focus on the belts used to drive the two axes; these are often prone to shedding lots of particulate. Avoid using excessive IPA near electronics. 

**Step 2.3.3: Place Scanner Inside Enclosure**

Remove all magnetic front panels from the enclosure and place the scanner inside the enclsoure. The LCD panel on the scanner should face the the front opening (where all the magnetic front panels just were). Center the scanner in the middle of the enclosure (left-to-right and front-to-back). Verify the scanner is properly positioned by slowly moving the bed front to back. It should be able to travel its entire length without hitting the back of the enclsoure or passing outside the front (where the magnetic panels would be mounted).

**Step 2.3.4: Plug in the Scanner**

Pass the 3D printer's power supply through one of the rounded rectangular ports on the bottom back left and right side of the 

## Step 3: Scripting

### Scription Overview

*Download the GitHub repo to your computer to access and run the scripts*

After fabricating the VPD scanner, you need to control it. The printer runs on GCODE, a human-readable, tool-control language where each line corrosponds to motor movements (or modification to a movement). There are three options for generating GCODE files, each with greater flexibility at the cost of greater complexity:

<details>
  <summary> Click here for Pre-generated Routine instructions (easiest) (recommended): <br></br></summary>

  ### Pre-Generated Routines

  Pre-generated routines are, as the name suggests, scan programs that have already been written and tested on the scanner. All testing, characterization, and normal operation of the VPD can be run from the pre-generated routines provided in this GitHub. The pre-generated routines require no programming or terminal commands.

  Within the 'pregenerated_routines' folder are six scan routines for different sized wafers. The size in the name of routine is the size of the wafer being scanned:

  - 1_inch_wafer_scan_pre_generated.gcode
  - 2_inch_wafer_scan_pre_generated.gcode
  - 3_inch_wafer_scan_pre_generated.gcode
  - 4_inch_wafer_scan_pre_generated.gcode
  - 5_inch_wafer_scan_pre_generated.gcode
  - 6_inch_wafer_scan_pre_generated.gcode

  The pre-generated routines have the following parameters:
  - Scan pattern: concentration starting in middle
  - Droplet volume: 300 uL
  - Scan speed: 175 mm/min
  - Scan height: 200 um
  - Droplet width: 5 mm

  To use the pre-generated routines, just make sure you've downloaded the GitHub repo.

  Follow the the instructions in 'Uploading Routines to the Scanner' to send the regenerated routine to the scanner. 

  **Only reason not to use pre-generated routine:** As mentioned above, we strongly recommend using the pre-generated scan routines, with the one exception of scanners built on any printer aside from the Ender 3; other 3D printers will have different physical travel limits which means using a default scan could crash the syringe into the print bed. If a different printer is being used, you'll need to create a Custom Routine.

</details>

<details>
  <summary> Click here for Re-Generated Routine instructions (more difficult): <br></br></summary>

  ### Regenerated Routines

  Regenerated routines are scan programs that are generated by the user using the regenerate_scan.py Python script provided in the GitHub repo. After executing the script with the desired custom parameters, the script will produce a program file which can be uploaded to the scanner. 

  To regenerate a routine based on your desired parameters, first ensure you've downloaded the GitHub repo. Navigate to the 'regenerated_routines' directory in terminal. For example...

  ```console
  foo@bar: cd /Users/thomas-rimer/Desktop/DIY-VPD/regenerated_routines
  ```

  To ensure you're in the right directory, type

  ```console
  foo@bar: ls
  ```

  which lists all files in your current directory. You should see 'regenerate_default_scan.py' as the only file to show up.

  Next call the 'regenerate_default_scan.py' along with the six required flags, explained below:

  | Flag Name                | Details                   |
  |-------------------------|-----------------------------------------|
  | filename | **Description**: name of the GCODE file saved to disk <br> **Units**: string <br> **Range**: <256 characters, just letters, numbers, and underscores |
  | droplet_volume | **Description**: volume of the droplet used to scan the wafer <br> **Units**: mL <br> **Range**: anywhere between 0.001 and 1 |
  | wipe_speed | **Description**: scan speed of the syringe over the wafer <br> **Units**: mm/min <br> **Range**: anywhere between 0.001 and 10000 |
  | wipe_height | **Description**: height of the syringe above the wafer while scanning <br> **Units**: mm <br> **Range**: any value above 0 |
  | droplet_width | **Description**:  width of the droplet formed on the surface of the wafer <br> **Units**: mm <br> **Range**: any value above 0 <br> **NOTE**: you must physically measure this value with calipers. guess 5mm the first time you generate the script, then revise based on measurement. |
  | wafer_size | **Description**:  diameter of the wafer to be scanned <br> **Units**: mm <br> **Range**: anywhere between 1 and 150 |

  An example call might look like

  ```console
  foo@bar: python3 regenerate_default_scan.py --filename=myCustomScan --droplet_volume=0.1 --wipe_speed=150 --wipe_height=0.3 --droplet_width=4.7 --wafer_size=150
  ```

  After calling this in terminal, a GCODE file with the entered filename (i.e. 'myCustomScan.gcode') will be created in the 'regenerated_routines' directory. If there is already a GCODE file with the same name, it will be overwritten.

  Follow the the instructions in 'Uploading Routines to the Scanner' to send the regenerated routine to the scanner. 

</details>

<details>
  <summary> Click here for Custom Routine instructions (most difficult): <br></br></summary>

  ### Custom Routine

  If you would like to write your own custom scan routine, you can with the 'generate_custom_routine' script in the same folder. This will allow you to create a routine with any sort of movement, aspiration, or dispensing. A custom routine requires several (10+) lines of python and a terminal command.

  *TODO: Write detailed instructions for how to generate Custom Routine*

</details>

### Uploading Routines to the Scanner

The scanner uses the original 3D printer interface to run routines. Routines are saved in the file format GCODE. To upload a routine (i.e. GCODE file) to the scanner

1) Plug the micro sd card into your computer using the provided micro sd to usb adapter.
2) If it's your first time uploading a routine, delete all existing files (if there are any) on the sd card.
3) Transfer desired gcode files from the pregenerated, regenerated, or custom folder onto the sd card (depending on which route you took). For example, if you plan on using just pregenerated routines (recommended) on 4" and 6" wafers, just upload '4_inch_wafer_scan_pre_generated.gcode' and '6_inch_wafer_scan_pre_generated.gcode' to the SD card.
4) Eject the sd card from your computer and plug it into the micro sd port on the front, bottom, left black controller box (underneath the scan bed).

The GCODE routines are now loaded on the printer and ready to run.

### Running Routines

To execute a routine that's been uploaded to the SD card:
1) **Turn on the scanner** (i.e. 3D printer) using the red power switch on the right side of its frame.
2) **Wait for the LCD to finish loading**. After a few loading screens the front LCD should show a home with some miscellanous information. This is all a remanant of the previous 3D printer operating system and is not relevant for the scanner. 
3) **Pull up the action menu** by pressing into the selection knob. It should click when pressed.
4) **Select "Print from SD"** by rotating the selection knob so the selection highlight is over "Print from SD." Press the knob again to select
5) **Select the desired scan routine to run** from the list of routines saved to the SD card. Use the same rotate and press selection method from above.

The scanner should begin the routine within a few seconds of selecting it.

## Step 4: Characterization

At this point, the scanner is ready to

*TODO: Explain how to perform a leach test. Explain our results*

*TODO: Explain how to perform a recovery test*

*TODO: Explain our recovery results*

## Step 5: Standard Operation

*Information about installment in a fumehood*

*How we process, store, and run tests with the SIGMA lab*

*Connecting to NEMO*

## Step 6: Misc

### License

This project is licensed under the MIT License. See the LICENSE file for more details.

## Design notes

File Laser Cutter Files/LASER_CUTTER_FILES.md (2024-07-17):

# Laser Cutter Files

Within the "Laser Cutter Files" folder are two subfolders:

* DXFs
* SVGs

Each of these subfolders has 8 files for each of the 8 acrylic side panels. The only difference between the two subfolders is the file format; they both contain the same designs. Use whichever file format is best for your laser cutter control program.

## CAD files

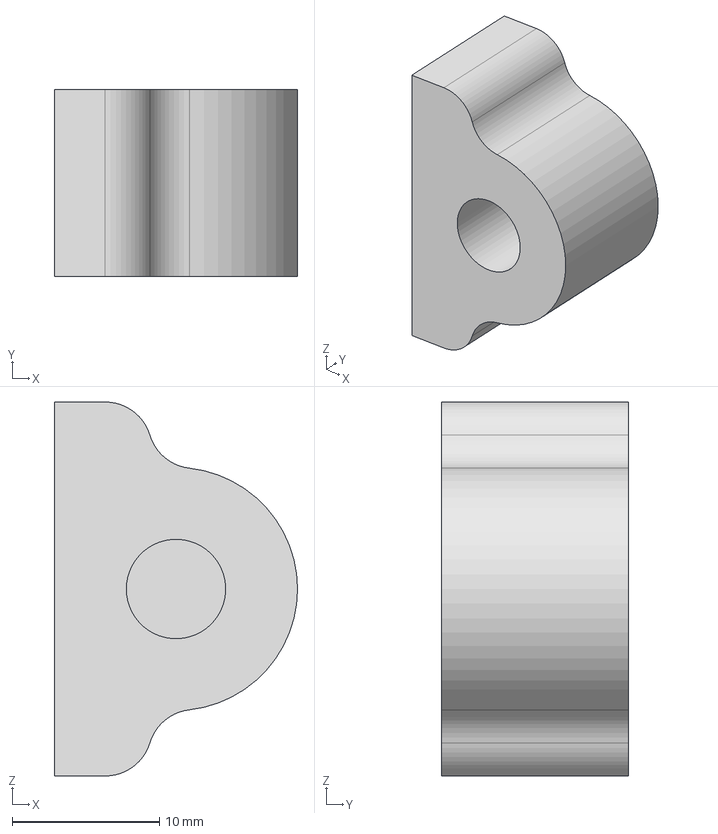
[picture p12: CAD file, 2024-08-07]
3D Printer Files/CAD Resources/magnet_mount.step
16.5 x 12.7 x 25.4 mm

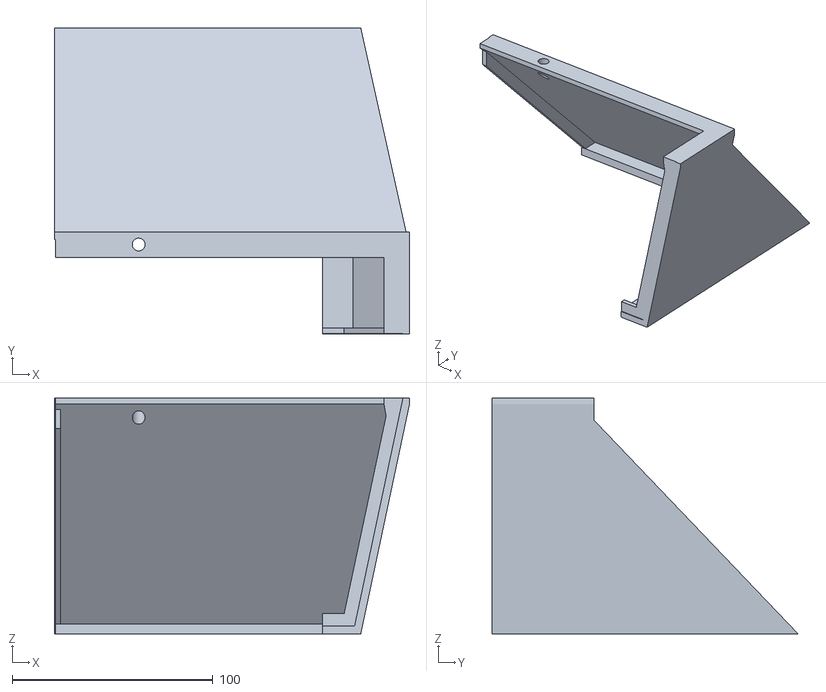
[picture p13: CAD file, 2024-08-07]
3D Printer Files/plenum_back_right.stl
176.7 x 152.4 x 117.3

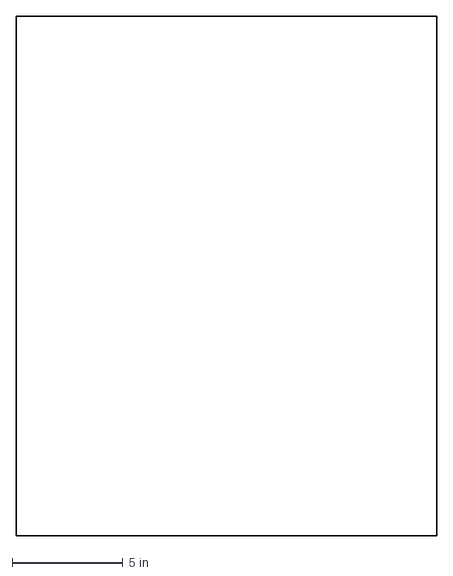
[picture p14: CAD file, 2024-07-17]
Laser Cutter Files/DXFs/bottom_panel.dxf
19.0 x 23.5 in

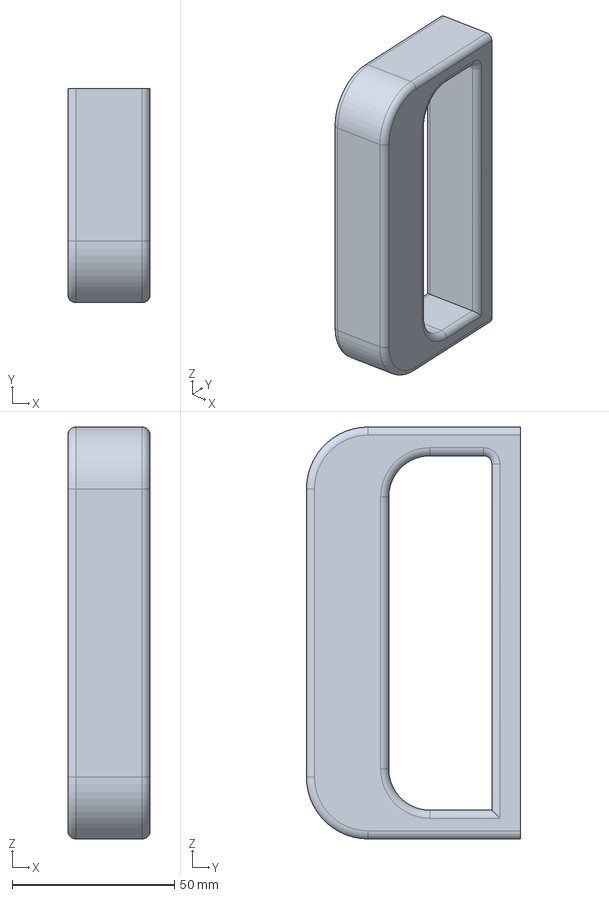
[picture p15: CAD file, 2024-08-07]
3D Printer Files/CAD Resources/handle.step
25.4 x 66.0 x 127.0 mm

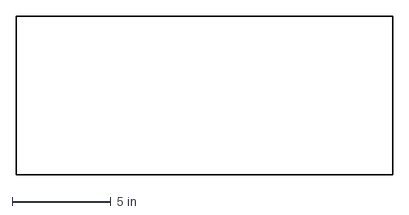
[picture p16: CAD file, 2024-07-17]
Laser Cutter Files/DXFs/front_middle_panel.dxf
19.0 x 8.00 in

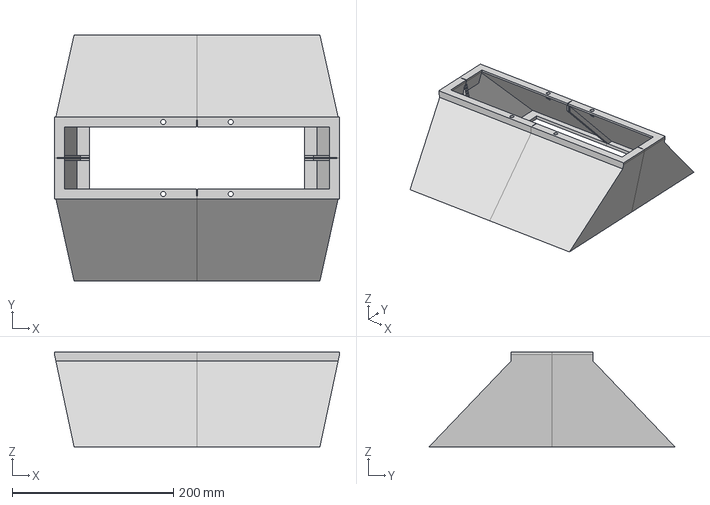
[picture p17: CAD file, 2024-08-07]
3D Printer Files/CAD Resources/plenum.step
353.3 x 304.8 x 117.3 mm

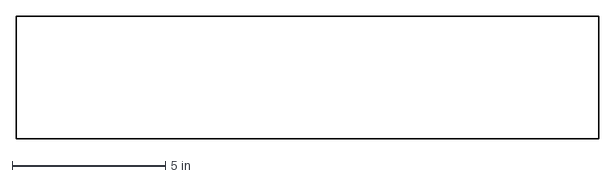
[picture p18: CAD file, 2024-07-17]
Laser Cutter Files/DXFs/front_bottom_panel.dxf
19.0 x 4.00 in

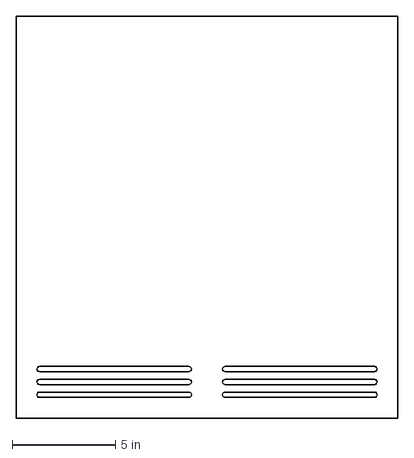
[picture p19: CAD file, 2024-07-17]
Laser Cutter Files/DXFs/back_panel.dxf
18.5 x 19.5 in

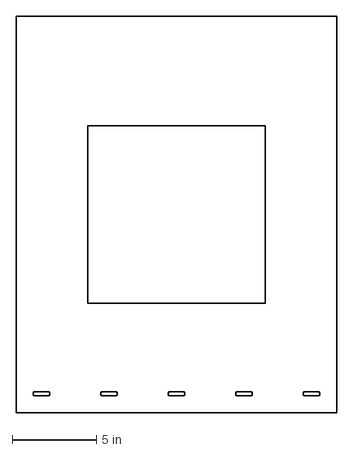
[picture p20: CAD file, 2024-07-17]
Laser Cutter Files/DXFs/top_panel.dxf
19.0 x 23.5 in

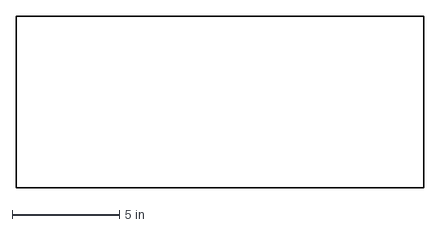
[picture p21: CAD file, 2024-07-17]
Laser Cutter Files/DXFs/front_top_panel.dxf
19.0 x 8.00 in

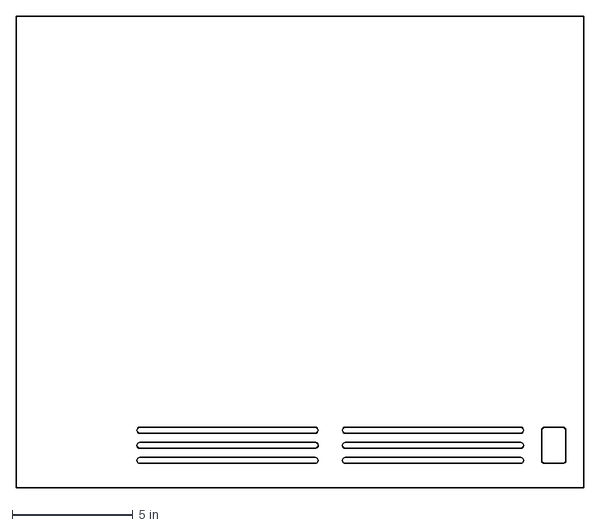
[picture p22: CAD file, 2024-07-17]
Laser Cutter Files/DXFs/right_panel.dxf
23.5 x 19.5 in

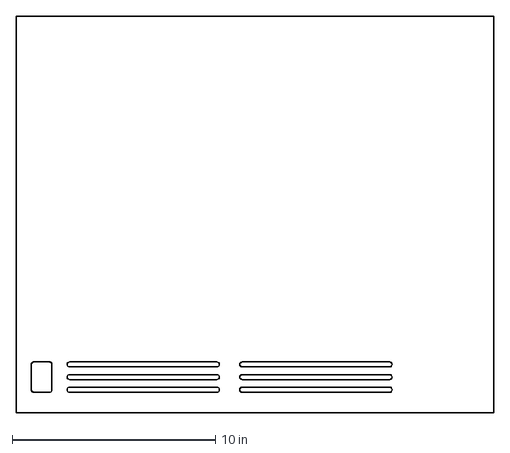
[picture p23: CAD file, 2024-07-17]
Laser Cutter Files/DXFs/left_panel.dxf
23.5 x 19.5 in

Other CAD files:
3D Printer Files/magnet_mount.stl
3D Printer Files/plenum_front_right.stl
3D Printer Files/plenum_front_left.stl
3D Printer Files/plenum_back_left.stl
3D Printer Files/handle.stl
3D Printer Files/CAD Resources/handle.f3d
3D Printer Files/CAD Resources/magnet_mount.f3d
3D Printer Files/CAD Resources/plenum.f3d

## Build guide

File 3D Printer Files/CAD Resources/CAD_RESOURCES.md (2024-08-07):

# CAD Resources

The "CAD Resources Folder" contains versions of all the 3D printer files in formats better suited to editing. **These files are only necessary if you want to edit or change the original designs.** If you just want to print the components, you can ignore everything in the CAD resources folder.

## .f3d

All 3D printed parts for the VPD were designed in Fusion360, whose native file format is .f3d. If you have access to Fusion360, we recommend using the .f3d files. These files retain timeline information making small edits extremely easy.

## .step

STEP files are a general CAD file format that work across every major CAD program. While editable, the lack of a timeline history makes tweaking small details difficult.

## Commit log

2024-07-17 added images to README, reorganized file structure
    [back_panel.dxf, bottom_panel.dxf, front_bottom_panel.dxf, front_middle_panel.dxf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]
2024-08-07 added plenum
    [handle.f3d, handle.step, handle.stl, magnet_mount.f3d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]
